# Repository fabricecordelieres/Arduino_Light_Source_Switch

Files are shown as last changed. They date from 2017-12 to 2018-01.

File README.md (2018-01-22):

# Arduino Light Source Switch

*This repository contains all the informations about the design of an automated light source switch for microscopy.*

Original idea, thinking and design: [Fabrice P. Cordelières](https://github.com/fabricecordelieres) and [Patrice Mascalchi](https://github.com/pmascalchi).

Special trick used to make the Arduino controllable from MicroManager by mimicking a device's communication protocol inspired by [Jérôme Mutterer](https://github.com/mutterer)

## Required parts

|Name|Link on Amazon.fr/Conrad.fr|Price (in euros)|Required|Actual cost (in euros)|
|---|---|---|---|---|
|PCB|[Copper Clad - TOOGOO(R) 10PCS FR4 Printed Circuit Laminate Board Single Sided Copper Clad PCB Fiber](https://www.amazon.fr/gp/product/B01DXF905Y/ref=oh_aui_search_detailpage?ie=UTF8&psc=1)|4.44|1|4.44|
|BluePrint transfer sheets|[5 feuilles PNP Blue pour circuits imprimés](http://www.conrad.fr/ce/fr/product/068815/5-feuilles-PNP-Blue-pour-circuits-imprims?queryFromSuggest=true)|19.99|1|4.00|
|Iron perchlorate|[Perchlorure de fer en granulé pour 1 litre d'eau](https://www.amazon.fr/perchlorure-fer-granul%C3%A9-pour-litre/dp/B004INQ4KK/ref=sr_1_2?ie=UTF8&qid=1514118209&sr=8-2&keywords=perchlorure+de+fer)|22.00|1|22.00|
|Arduino Nano|[Kuman 10 x Mini Nano V3.0 ATmega328P 5V 16M Micro Controller Board Module pour Arduino KY64-10](https://www.amazon.fr/gp/product/B01NCM5W9O/ref=oh_aui_detailpage_o08_s00?ie=UTF8&psc=1)|32,80|1|3.28|
|Stackable straight female pin headers for Arduino|[VAPKER 18 Type 2.54mm Single Row Empilable Femelle Pitch Straight Female Pin Header Kit Pour Arduino](https://www.amazon.fr/gp/product/B06XTMGWCL/ref=oh_aui_detailpage_o03_s00?ie=UTF8&psc=1)|7.92|1|3.96|
|Green & Red LEDs|[Elegoo 3mm et 5mm Diffusé et Transparent le Kit LED Diode Electro Luminescente Assorti 5 Couleurs pour Arduino (Pack de 600)](https://www.amazon.fr/gp/product/B073CYK8X5/ref=oh_aui_detailpage_o04_s00?ie=UTF8&psc=1)|10.99|2|0.04|
|220 Ohms and 2.2 KOhms resistors|[Elegoo 17 Values 1% Assortiment de Kit de Resistor 0 Ohm-1M Ohm (Pack of 525) avec Boîte en Plastique pour Arduino et Projet Expérimental](https://www.amazon.fr/Elegoo-Assortiment-Resistor-Plastique-Exp%C3%A9rimental/dp/B071LHFQKD/ref=sr_1_1?ie=UTF8&qid=1514118669&sr=8-1&keywords=resistances)|9.99|1|0.04|
|Push button|[SODIAL(R) 5 x Momentary SPST NO Red Round Cap Push Button Switch AC 6A/125V 3A/250V](https://www.amazon.fr/gp/product/B00F4MGQU2/ref=oh_aui_search_detailpage?ie=UTF8&psc=1)|1.89|1|0.38|
|Servo|[Kuman KY66 Micro Servomoteur SG90 10pcs, 9G Robot Contrôle D'hélicoptère, Avion, Bateau, Mini Servo 450](https://www.amazon.fr/gp/product/B01MXPTCHO/ref=oh_aui_detailpage_o05_s00?ie=UTF8&psc=1)|23.00|1|2.30|
|2.9mmx13mm screws|[uxcell 2.9mmx13mm Phillips Round Head Self Tapping Screws 50 Pcs](https://www.amazon.fr/sourcingmap%C2%AE-2-9Mmx13mm-inoxydable-cruciforme-autotaraudeuses/dp/B019ETFW7I/ref=sr_1_fkmr0_1?ie=UTF8&qid=1514660189&sr=8-1-fkmr0&keywords=2.9mmx13mm+s)|10.10|2|0.40|
|USB Cable|[AmazonBasics USB 2.0 Cable - A-Male to Mini-B - 6 Feet (1.8 Meters)](https://www.amazon.fr/gp/product/B00NH11N5A/ref=oh_aui_detailpage_o04_s00?ie=UTF8&psc=1)|5.95|1|5.95|
|PLA Filament Transparent|[XYZprinting RFPLCXEU06C PLA Filament(NFC), 600 g, white, 200m](https://www.amazon.fr/gp/product/B0142FW8W6/ref=oh_aui_detailpage_o06_s00?ie=UTF8&th=1)|34.27|1.29m|0.22|
|PLA Filament Black|[XYZprinting RFPLCXEU01B PLA Filament(NFC), 600 g, black, 200m](https://www.amazon.fr/gp/product/B00WHQ9XRQ/ref=oh_aui_detailpage_o06_s00?ie=UTF8&psc=1)|29.90|19.56m|2.92|
|Super glue|[Loctite Colle forte/ Super Glue 3 - Universal - 3 g - Lot de 2](https://www.amazon.fr/Loctite-Colle-forte-Super-Glue/dp/B008F7YFS8/ref=sr_1_1?ie=UTF8&qid=1514664075&sr=8-1&keywords=super+glue)|5.75|1|2.87|
|**Total**||**218.99**||**52.80**|

## Required tools

|Name|Link on Amazon.fr|Price (in euros)|
|---|---|---|
|Dremel|[Dremel 3000-15 Outil rotatif multi-usage (130W) 1 sac et 15 accessoires](https://www.amazon.fr/Dremel-3000-15-rotatif-multi-usage-accessoires/dp/B0073R1IZ4/ref=sr_1_1?s=industrial&ie=UTF8&qid=1514662535&sr=1-1&keywords=dremel)|39.99|
|Dremel Stand|[Dremel 26150220JB drill press & tool holder for dremel tools 200-5, 4000-1/45, 4000-4/65](https://www.amazon.fr/Dremel-Support-Workstation-multifonctions-26150220JB/dp/B0012RQG94/ref=sr_1_8?s=industrial&ie=UTF8&qid=1514662535&sr=1-8&keywords=dremel)|52.16|
|Drill|[Dremel 628-01 7 Piece Drill Bit Set by Dremel](https://www.amazon.fr/Dremel-628-01-Piece-Drill-Bit/dp/B0000302Z3/ref=sr_1_cc_6?s=aps&ie=UTF8&qid=1514663038&sr=1-6-catcorr&keywords=foret+dremel)|20.73|
|Soldering iron|[HOMASY Kit de Fer à Souder Réglable 60W Soudage Electrique avec 5 PCS Points Différents, Pompe à Dessouder, Support, Brucelles anti-statiques et Fil de Soudure](https://www.amazon.fr/gp/product/B01HY1A26Y/ref=oh_aui_search_detailpage?ie=UTF8&psc=1)|18.59|
|3D printer|[XYZprinting 3FM1WXEU00H Imprimante da Vinci Mini W](https://www.amazon.fr/XYZprinting-3FM1WXEU00H-Imprimante-Vinci-Mini/dp/B01KJEWO28/ref=sr_1_1?s=hi&ie=UTF8&qid=1514666367&sr=8-1&keywords=da+vinci+mini)|281,85|
|Cutter|[Wedo Hobby Knife Set - Silver](https://www.amazon.fr/Wedo-078722-couteau-bricolage-recHange/dp/B001ALYPY0/ref=sr_1_2?ie=UTF8&qid=1514662864&sr=8-2&keywords=cutter+de+pr%C3%A9cision)|6.40|
|Screw drivers|[Zacro 25pcs Tournevis de Multi-usages Tournevis de Précision Set Outils de Réparation pour Téléphone, Mobile Phone, iPhone 5, 5s ,6s, Samsung, HTC, Nokia, Laptop ,Computer, Macboo](https://www.amazon.fr/gp/product/B01M3RZ9OR/ref=oh_aui_search_detailpage?ie=UTF8&psc=1)|6.99|
|Tin/lead solder|[Silverline Solder 100g](https://www.amazon.fr/Silverline-AS15-Bobine-d%C3%A9tain-soudure/dp/B000LFTN1G/ref=sr_1_2?s=hi&ie=UTF8&qid=1514663169&sr=1-2&keywords=etain+a+souder+%C3%A9lectronique)|8.65|
|**Total**||**435.36**|

## How does it work ?

### Electronic design

The electronic design is pretty simple. A [Fritzing scheme](FreeCAD/Arduino-Light_Source_Switch.FCStd) is enclosed in this repository:

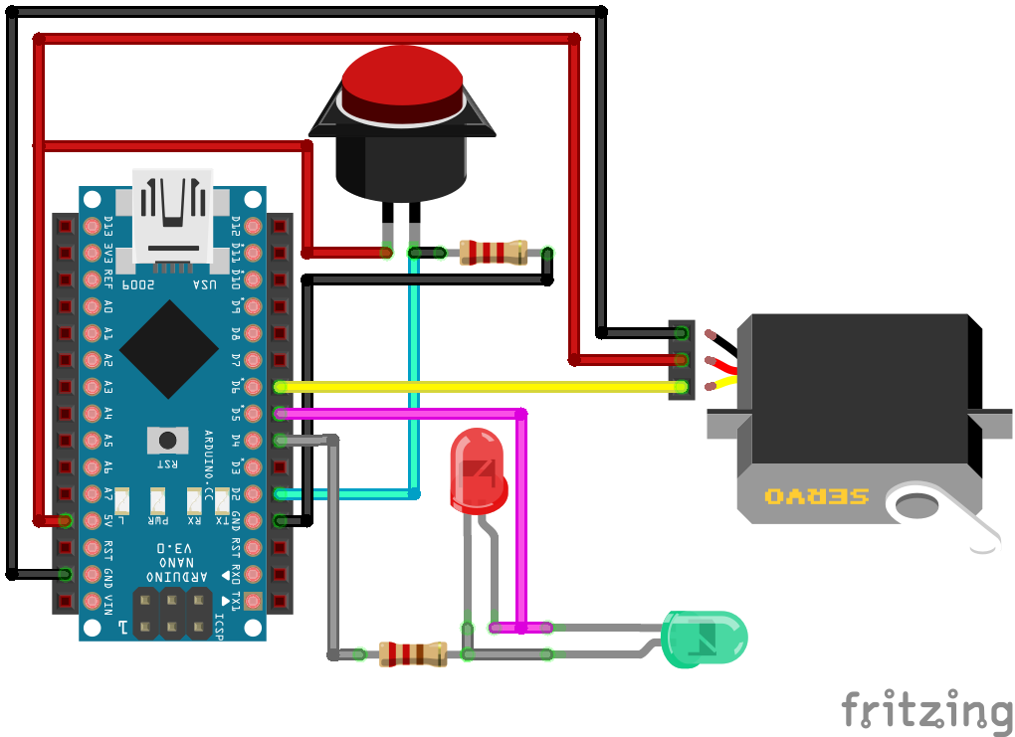
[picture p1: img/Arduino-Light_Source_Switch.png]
Fritzing diagram


#### Push-down button
The push-down button is connected to the Arduino's +5V power supply on one side. the other side is connected to both the ground through a *2.2 KOhms resitor* and to the Arduino's *D2 digital pin*. This configuration is called *pull-down mode*, as when no action is performed, the current is pulled-down to the ground using the resistor. When the button is pushed, the current is drained towards the D2 pin. The state can be read as *HIGH state* on the digital port.

#### LED indicators
Two LEDs, one red, the other one green are connected to both the Arduino's *D4 and D5 digital pins* through a *220 Ohms resistor*. They are both connected in a head-to-tail fashion: if D4's state is HIGH and D5's is LOW, the red LED will shine, but not the green one, and the reverse way round. This tricks allows only using 2 digital pins and not using the ground pin to shine one LED at a time.

#### Servo
Nothing really specific about the servo: it's connected to both the Arduino's +5V power supply and ground. It's signal pin is connected to the Arduino's *D6 digital pin*. As only one servo is required which specifications are not really demanding, choice was made to power it through the computer's USB socket.

### Circuit assembly

Circuit assembly is straightforward. As depicted on the following diagram, the Arduino is connected through pin headers. In between the two, three wires allows connecting to the servo. Two additional wires are soldered to the push-button. On the right side, the two LEDs are implanted head-to-tail. Two resistors are also present on the PCB: the top one to protect the LEDs (220 Ohms), the bottom one being the pull-down resistor used on the push-down button circuit (2.2 KOhms).

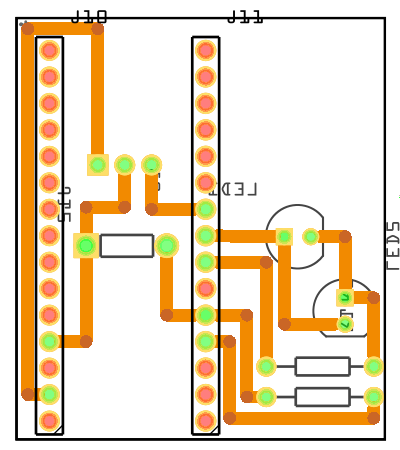
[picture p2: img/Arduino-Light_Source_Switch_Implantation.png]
Implantation diagram


### 3D printed parts
A [FreeCAD file](FreeCAD/Arduino-Light_Source_Switch.FCStd) and [STL files](STL/) are provided as part of this repository, allowing to print the enclosure for the circuit board, the support for the servo and the slider.

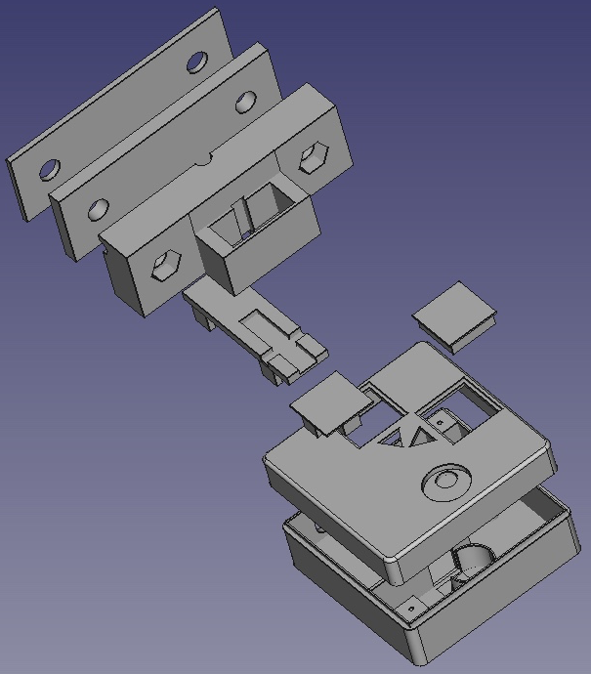
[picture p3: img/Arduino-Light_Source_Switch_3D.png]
3D printed parts


For informational purposes, the time required to print part and the length of PLA used is provided in the following table. The numbers have been recorded using a [Da Vinci mini 3D printer](https://www.amazon.fr/XYZprinting-3FM1WXEU00H-Imprimante-Vinci-Mini/dp/B01KJEWO28/ref=sr_1_1?s=hi&ie=UTF8&qid=1514666367&sr=8-1&keywords=da+vinci+mini):

|Part|Time required for printing|Length of PLA needed|Color|
|---|---|---|---|
|Windows|00:43|1.29m|White|
|Bottom case|05:05|7.71m|Black|
|Top case|03:05|5.08m|Black|
|Servo's support, spacers and slider|04:19|6.77m|Black|
|**Total**|**13:15**|**20.85m**|**All**|

### Programming
A [Arduino script](Arduino/Arduino-Light_Source_Switch.ino) is available form the repository. It basically handles the input from two sources:
* *From the button:* it switches the servo from the right to the left position and the reverse way round. The boolean variable "isRight" keeps track of the current position;
* *From the serial input:* sending 64, 66, 68 or 70 will turn the servo to the right position; while sending 65, 67, 69 or 71 will turn it to the left position. This communication protocol emulates the behavior of a [Vincent Associates VMM-D3 Shutter Driver](https://www.uniblitz.com/products/vmm-d3-shutter-driver/). It therefore allows this device to be integrated and driven by softwares such as [Micro-Manager](https://micro-manager.org/).

### Setup/first tests
From the first tests, two types of problems might arise:
* *Right/left positions are not correct:* in such cases, adapt the [Arduino script](Arduino/Arduino-Light Source Switch.ino) by tweaking the ```rightPosition``` and ```leftPosition``` variables' values;
* *Pressing once the button will make the slider move quickly right-left-right or left-right-right:* you should adapt the refractory period in the [Arduino script](Arduino/Arduino-Light_Source_Switch.ino) by modifying the ```timeout``` variable' value.

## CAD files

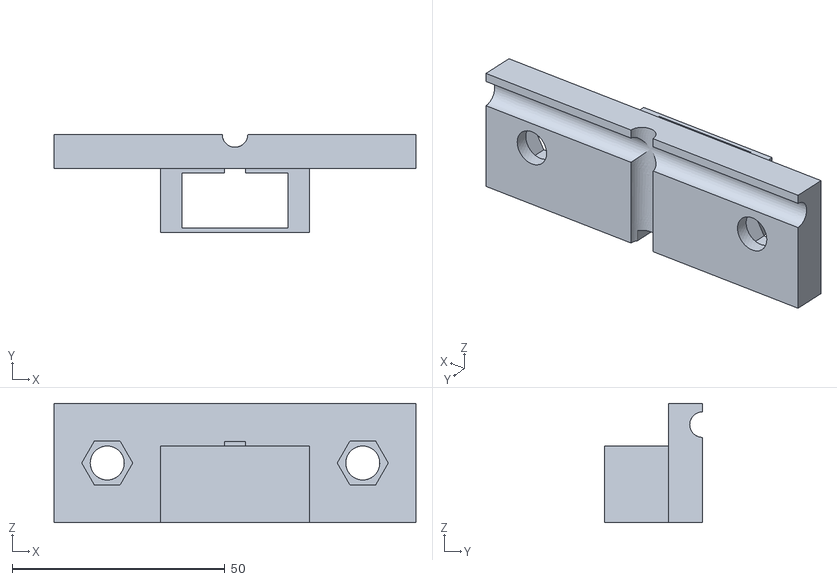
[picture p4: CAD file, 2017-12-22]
STL/Servo_Support.stl
85.0 x 23.0 x 28.0

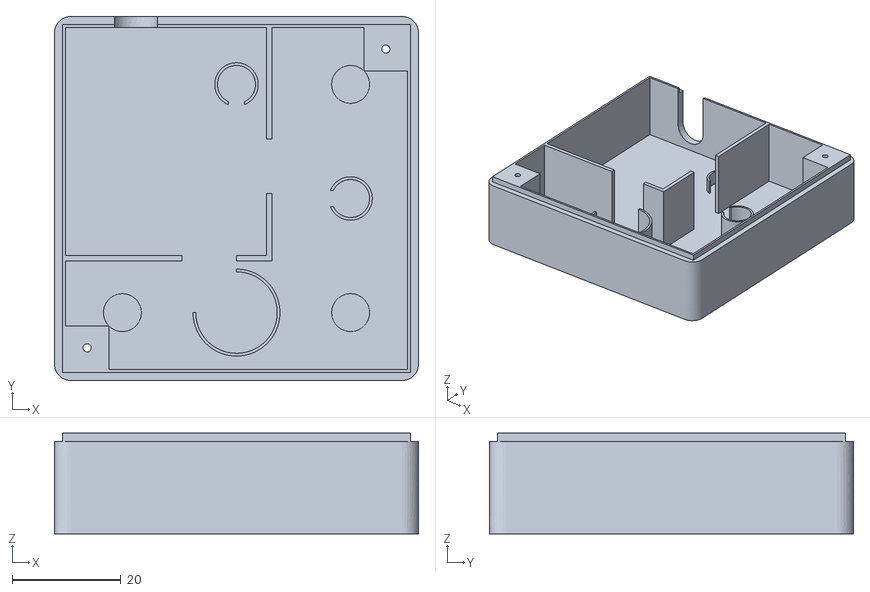
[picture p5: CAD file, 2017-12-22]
STL/Case_Bottom.stl
67.0 x 67.0 x 18.5

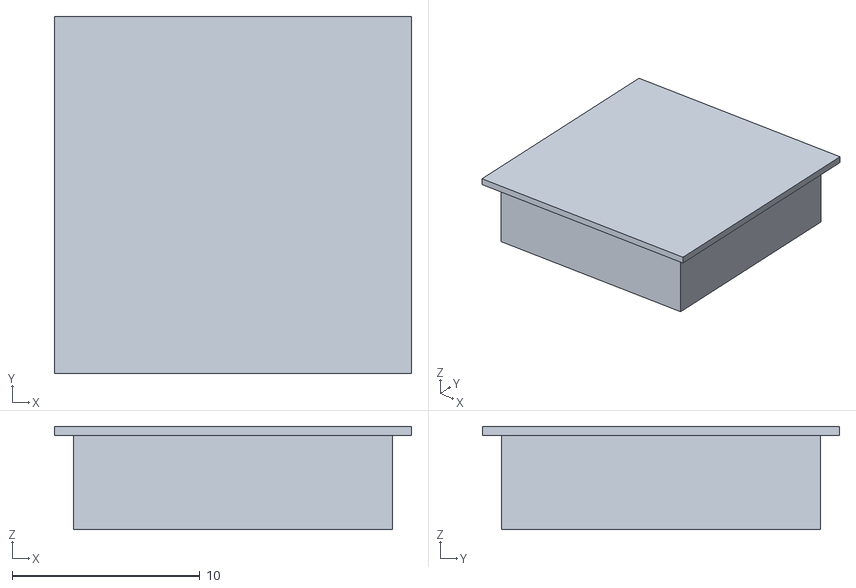
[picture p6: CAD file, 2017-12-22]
STL/Window_LED.stl
19.0 x 19.0 x 5.50

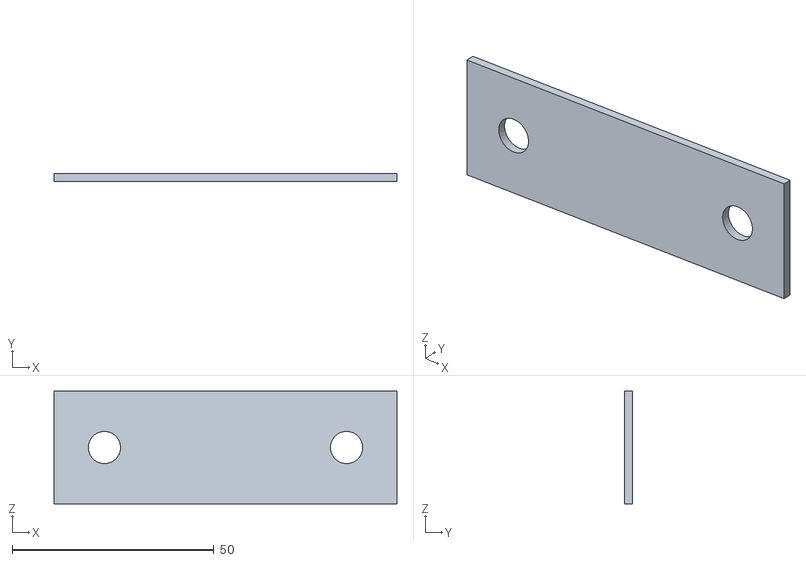
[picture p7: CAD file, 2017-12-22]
STL/Servo_Support-Spacer_2mm.stl
85.0 x 2.00 x 28.0

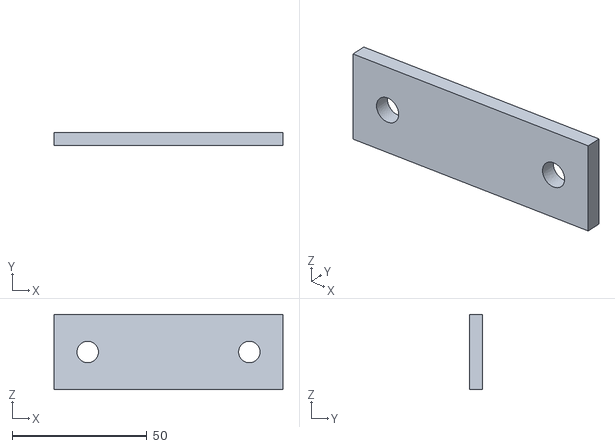
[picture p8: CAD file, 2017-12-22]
STL/Servo_Support-Spacer_5mm.stl
85.0 x 5.00 x 28.0

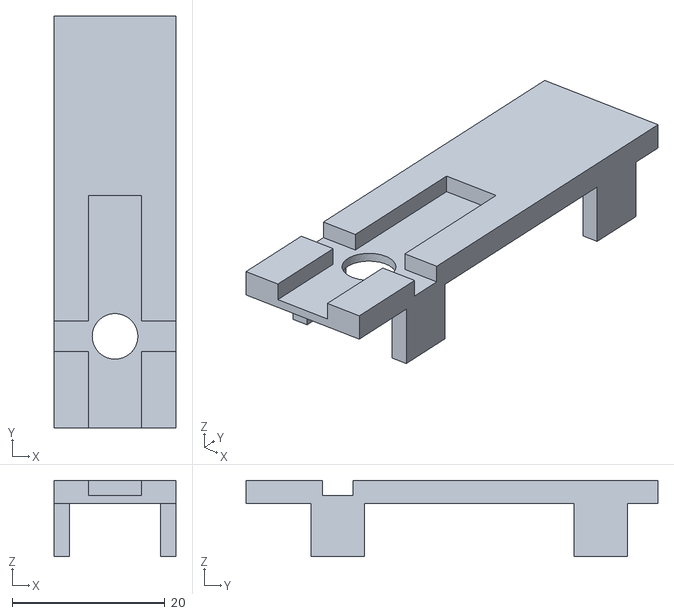
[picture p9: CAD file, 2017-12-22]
STL/Servo_Slider.stl
16.0 x 54.0 x 10.0

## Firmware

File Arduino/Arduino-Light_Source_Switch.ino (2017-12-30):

//Digital pin 2: Switch
//Digital pin 4 & 5: LED
//Digital pin 6: Servo

#include <Servo.h>

boolean isRight=false; //True if the output is on the right
int readValue=0; //Push button's status
int inByte = 0; //Incoming serial byte
int rightPosition=37; //Angle of the servo to push/pull the lever to the right
int leftPosition=97; //Angle of the servo to push/pull the lever to the left
int timeOut=250; //Refractory period: won't answer in case an action is fired less than XXX msec fro mthe previous one


Servo myservo;

void setup() {
  pinMode(2, INPUT);
  pinMode(4, OUTPUT);
  pinMode(5, OUTPUT);

  myservo.attach(6, rightPosition, leftPosition);
  changeSide(); //Initialises to the right side
  
  Serial.begin(9600);
  while (!Serial) {
    ; // wait for serial port to connect. Needed for native USB port only
  }  
}

// the loop function runs over and over again forever
void loop() {
  //Check action on the physical button
  readValue=digitalRead(2);
  if(readValue==HIGH){
    changeSide();
  }
  
  //Check for instructions on the serial port.
  //Uses the Vincent Unblitz VMM-D3/D4 communication protocol
  if (Serial.available() > 0) {
    //Get incoming byte:
    inByte = Serial.read();
    
    //Check for open channel 1, 2, 3 or all
    if(inByte==64 || inByte==66 || inByte==68 || inByte==70){
      isRight=true;
      changeSide();
    }
    
    //Check for close channel 1, 2, 3 or all
    if(inByte==65 || inByte==67 || inByte==69 || inByte==71){
      isRight=false;
      changeSide();
    }
  }
  delay(timeout);
}

// Changes the side of the switch
void changeSide(){
  isRight=!isRight;
  if(isRight==true){
    digitalWrite(4, HIGH);
    digitalWrite(5, LOW);
    myservo.write(rightPosition);
  }else{
    digitalWrite(4, LOW);
    digitalWrite(5, HIGH);
    myservo.write(leftPosition);
  }
  delay(timeOut);
}

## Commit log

2017-12-30 Update Arduino-Light Source Switch.ino
2017-12-30 Rename Arduino-Light Source Switch.ino to Arduino-Light_Source_Switch.ino
